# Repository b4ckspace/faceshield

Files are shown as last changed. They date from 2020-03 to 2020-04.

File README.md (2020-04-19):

# Lasercut Face Shield

Due to the Covid-19 outbreak, there is an increased need for face protection for health care professionals and many others. There are multiple projects that are trying to offer makeshift solutions. These are ours.

Our face shields are laser cut which allows producing lots of shields quickly. What makes our v1 and v2 shields different is that we are not cutting the actual shield but use off the shelf A4 or A3 transparency sheets. That way the laser cut pieces can be reused multiple times while only replacing the transparency shield. This is not a new idea but other projects offering this feature are all 3D printed which limits the output.

The sheet is attached with standard pattern holes that can be created with a normal 80mm, Euro pattern hole puncher. Support for 888 patterns or full 4 hole punchers are of benefit.

See our [detailed instructions](hole_patterns.md) on how to create these hole patterns.

## Version 1
Still primitive, uses hollow rivets for construction
Shield Version 1
[Details](v1/)

## Version 2
More sophisticated. Comes with a shield for the fore head. Is more flat at the front. No needs for fasteners.
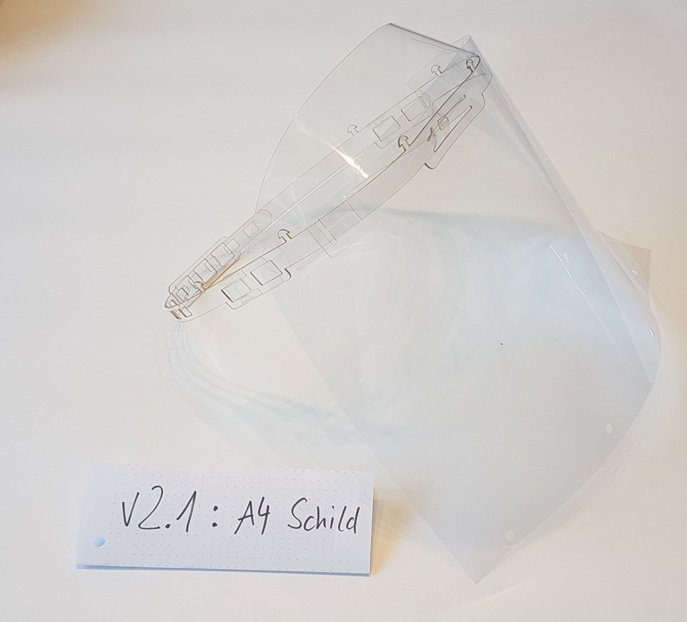
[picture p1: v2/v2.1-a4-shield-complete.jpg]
Shield Version 2.1

[Details](v2/)

## Version 3
A full shield cut from thicker material (0.7mm PET and 0.8mm PP).
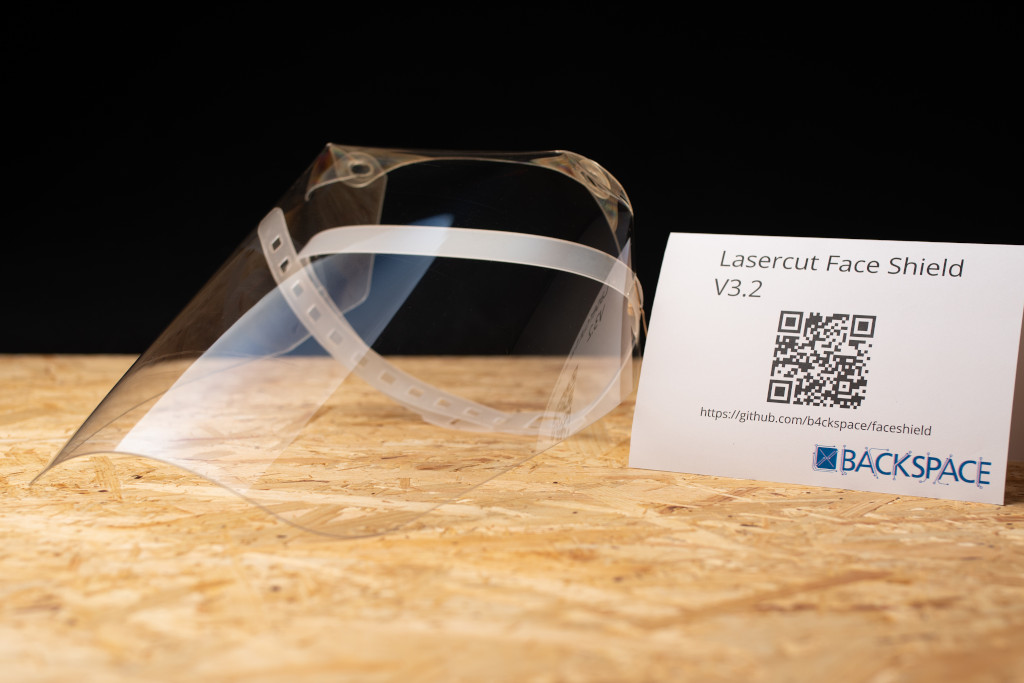
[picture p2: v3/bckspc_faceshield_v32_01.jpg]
Shield V3.2


[Details](v3/)

## Shield from Office Supplies
A shield made only out of an A3 sheets with normal office supplies. No need for a laser cutter or other exotic tools.
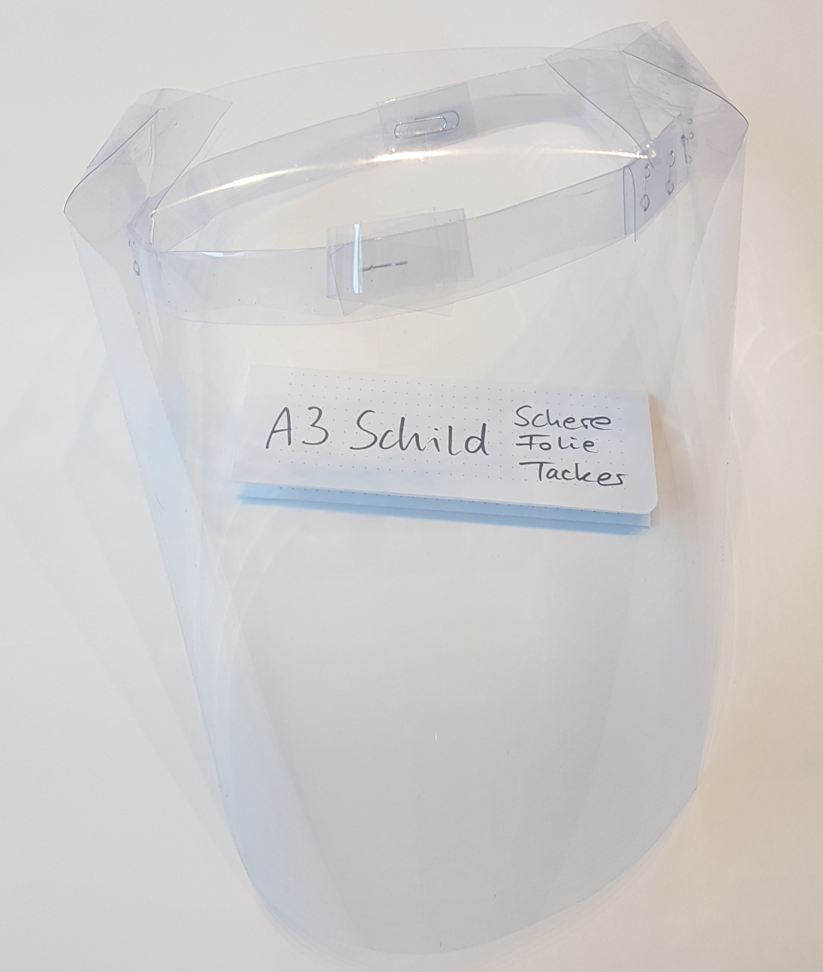
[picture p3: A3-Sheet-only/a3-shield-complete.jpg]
A3 Shield


[Build instructions](A3-Sheet-only/manual.md)

## Status

All variants work quite well, but they depend a lot on the materials used. The different plastics cut and behave quite differently. Polycarbonate ist really tough and cuts well but produces a huge mess and clogs up the filters really fast. The 0.69mm PET has good optical quality but tends to be brittle and a lot of fancy features had to be abandoned for v3 as the material would just break too easily. We are currently using 0.8mm Polypropylene as head straps as it is soft and does not break. This works fine for V3 but might not be stiff enough for an unsupported arc holding an heavy shield in front of the face.

The lesson learned here is that each new material basically requires some new engineering effort.

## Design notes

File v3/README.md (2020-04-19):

# Laser Cut Face Shield V3.2

Shield 3.2

This variant is optimized for the material we had at hand: 0.69mm PET. It is still unclear what is the exact cause but our material tends to break in a brittle way - sometimes. This forces this model to be more primitive and to avoid more clever solutions.

The shield consists of two laser cut parts: The shield itself, made from 0.69mm PET that gets folded inwards at the top and the head strap made from 0.8mm PP which is much softer.

V3.2 cutting pattern

They are connected with two split pin paper fasteners. While they look very unfomfortable they actually barely touch the head of the wearer.

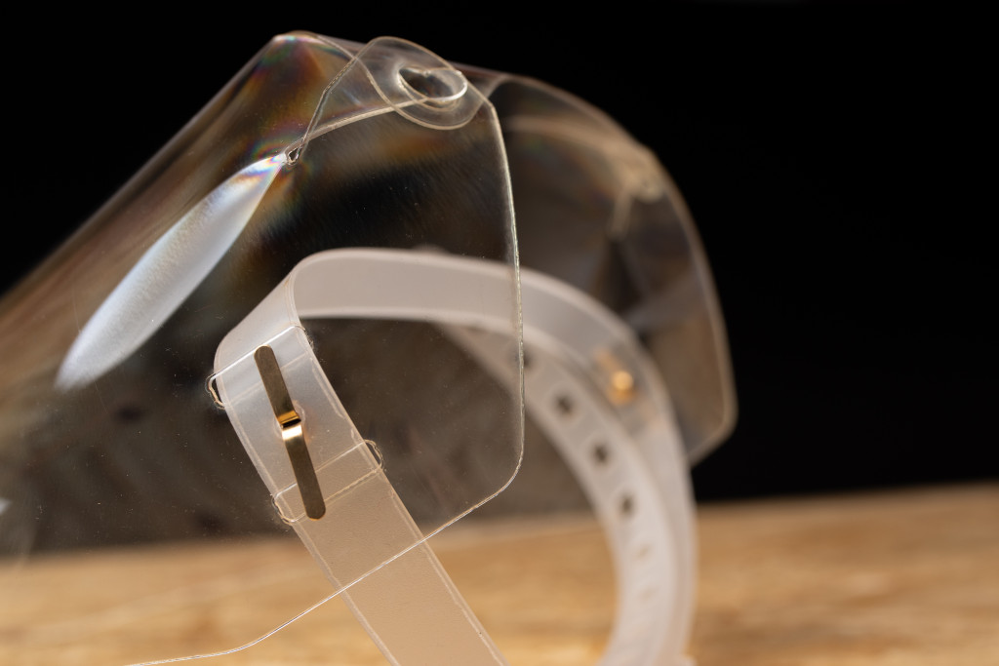
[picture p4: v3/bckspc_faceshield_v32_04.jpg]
Shield details


What sets this shield appart from others:

The shield is bend inwards at the top. This reduces the gap between the shield and the head. It also stiffens the shield and keeps it more flat at the front. This makes it easier to see through and reduces reflections and glares.

No elastic band used. This makes it easier to desinfect. It also allows putting it on with only one hand. So it may be more conviniet in situations where the shield needs to be put on and off very often or very quickly. Size of the head strap can be adjusted easily. The current material we use is on the soft side for this mechanism. It works even better with stiffer materials - either thicker PP or other plastics like PC or PS.

There are multiple intermediate versions that use more clever ways of construction and don't need additional hardware. We will publish them here soon.

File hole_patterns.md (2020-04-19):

# Creating The Right Hole Patterns

Version 1 and 2 are both supporting A4 and A3 sheets. But other sizes can also be used if given the right hole patterns. The basic pattern we use is called 888 or 3x8 and is supported on most Euro hole punchers. This is a pattern of 4 holes with 80mm distance center to center. There are a lot of ways to achive this pattern - depending on the equippement at hand.

## 4 Hole punch

If you need a lot of sheets (e.g. you want to change them often) get a normal 4 hole punch. They are cheap and create the pattern right away.

## Normal 2 Hole Punch With Side Stop

Many hole punchers have an adjustable side stop that does have an 888 or 3x8 setting. You can just use this setting from both sides of the page to get the 4 holes all with the same distance. This **only works** for sheets that are **exaclty A4** in size!

## Measure

You can use a ruler to find the right place to punch the holes. As normal hole punchers typically have a mark for the center of the page you can just mark the spots 80mm left and righ of the page center and align your hole punch there. This has the benefit of also working with sheets that are not 297mm long (A4 landscape)

## Double punch!

If you just have a normal hole punch you can try this:

* Mark the middle of the page
* Punch the center holes
* Use the holes as new centers
* Use the new outer holes as new centers

This gives you a row of holes 40mm apart. Some of them are punched twice. You need to be pretty precise for this to work. Check if the double holes are not missaligned

## A3 Sheets

For the A3 we use the (fictional) 88888 pattern. It is the 888 pattern from above plus two more holes that are also 80mm further out. If you want to use A3 sheets you really should get a 4 hole punch, but you can also use any other methods above - except using a side stop.

The outer holes would be 10mm in from the sides. We moved hooks inward a bit so holes with about 11mm from the sides also work. That way you can just turn you hole punch around and use it from the sides. The hole should be about the same distance from above.

# Other Holders

Note that not everyone is using this pattern. Some 3D printed shields use a 80mm-68.5mm-80mm pattern. It is created by using the A6 side stop settings from both sides on an A4 sheet.

Our design currently does not support this hole pattern. But it can be added easily. Please open a ticket if you are interested.

# Cutting To Shape

All sheets need to be cut into shape to allow head movement. A4 can be used uncut, but is much more comfortable if the lower corners are clipped. A4 sheets offer just enough protection for many use cases.

A3 sheets offer much better protection. But if used in their full size are just too big and don't let enough fresh air in. They need to be cut to size. You want to cut off the bottom corners up to the top edge and probably even shorten it at the bottom. It is difficult to give general advice here as all use cases are different.

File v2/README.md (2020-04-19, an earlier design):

# Face Shield Version 2

Shield V2.1

This also a holder for a transparent sheet. Both A4 and A3 sizes are supported. The two main parts need to be cut from a stiff material. 1 to 1.5mm thickness should work for plastics like Polycarbonate (PC), Polystylol (PS) or PETG. The fore head shield needs to be more elstic. We used .5mm PETG but this can surely be made from even thinner material.

Cuttingpattern

# Assembly

The short strap needs to be put through the inner rectangular holes until the wider part is on the outside. Then turn the strap upright so it cannot get out again. The thinner ends are then put to the next hole to lock the strap in place.

Connect the flaps at the front by twisting them an put the inner ends through the holes at the outside strap.

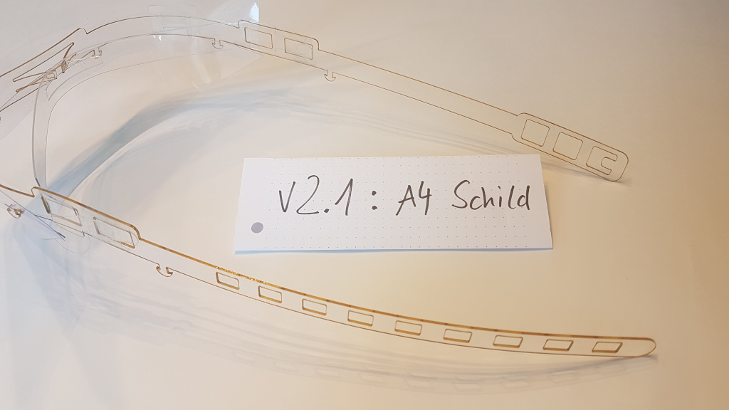
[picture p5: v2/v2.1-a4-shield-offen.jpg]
Details


If you want the front shield to be less round at the bottom you can put two of the small pieces with the mushrooms at the ends into holes on both sides. You need an 888 holes pattern at the bottom of the sheet for this (4 holes each 80mm appart). But we found that to not be necessary.

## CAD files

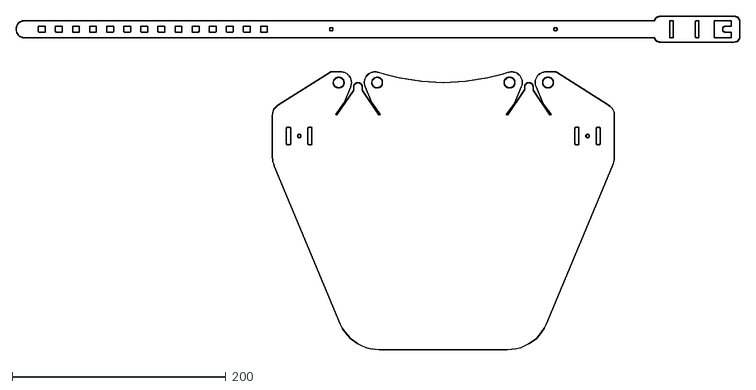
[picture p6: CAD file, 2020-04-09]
v3/faceshield-3.2.dxf
677.6 x 312.0

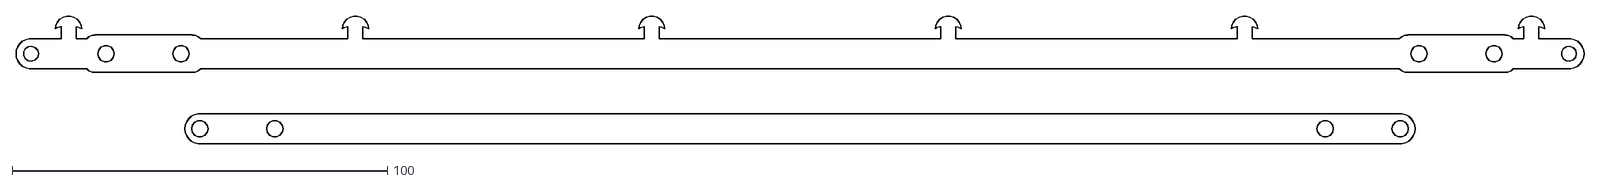
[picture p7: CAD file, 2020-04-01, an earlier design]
v1/faceshield.dxf
418.0 x 34.0

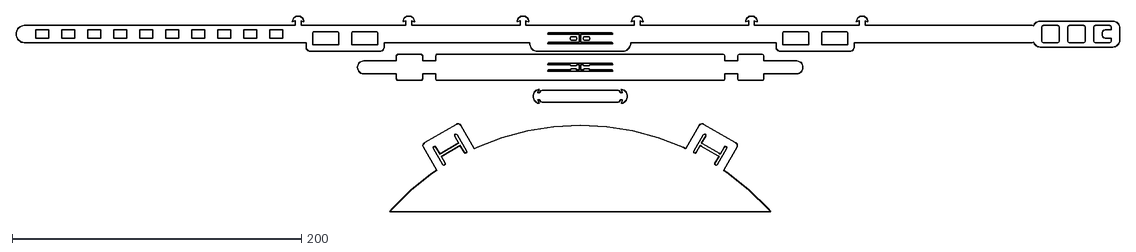
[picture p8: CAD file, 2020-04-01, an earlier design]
v2/faceshield-v2.1.dxf
763.2 x 135.5

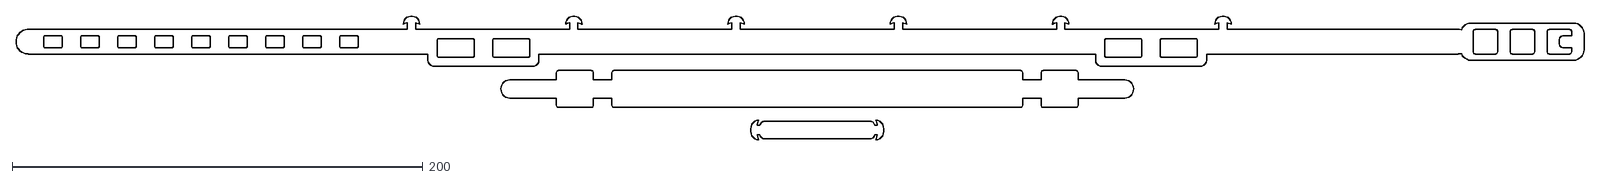
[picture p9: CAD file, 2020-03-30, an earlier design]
v2/faceshield.dxf
763.2 x 60.3

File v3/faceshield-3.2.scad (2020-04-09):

shield_width = 320;
shield_height = 220;

strap_length = 700;
strap_inner = 16;
strap_outer = 24;

$fa = 6;
$fs = .5;

module roundedRectangle(x, y, z, r) {
    difference() {
        cube([x, y, z], center=true);
        for (sx = [-1, 1]) {
           for (sy = [-1, 1]) {
              scale([sx, sy]) {
                translate([x/2, y/2])difference() {
                    cube([2*r, 2*r, 2*z], center=true);
                    translate([-r, -r])cylinder(3*z, r=r, center=true);
                }
              }
            }
        }
    }
}

module clip(wo, wi, f=.2) {
    difference() {
        roundedRectangle(3*wo+(wo-wi), wo, 1, 5);
        //for (x = [-1.5*wo+wi/2:wo/2:1.5*wo-wi/4])translate([x, 0, 0])roundedRectangle(wi/3, wi, 3, 1);
        translate([1*wo, 0, 0])difference() {
            roundedRectangle(wi, wi, 2, 1);
            translate([0.5*wi, 0, 0])roundedRectangle(wi, wi/3, 3, 2);
        }
        roundedRectangle(f*wi, wi, 2, 1);
        translate([-wo, 0, 0])roundedRectangle(f*wi, wi, 2, 1);
    }
}

module strap(lt, l, w, wi) {
    offset = 50;
    union() {
        difference() {
            union(){
                translate([-2*w-offset, 0])roundedRectangle(lt-4*w, wi, 1, wi/2);
                //roundedRectangle(l+40, w, 1, 5); // middle part
                translate([lt/2-2.6*w-offset, 0])clip(w, wi);
                /*
                for (msx = [-1, 1])scale([msx, 1, 1]) {
                    translate([l/2-45, 0, 0])roundedRectangle(20, wi+8, 1, 1);
                }*/
            }
            /*
            for (i = [-1, 1])for (j = [-1, 1])scale([i, j, 1]) {
                translate([l/2-15, wi/2+1])roundedRectangle(30, 2, 2, 1);
                translate([l/2-15, -(wi/2+1)])roundedRectangle(30, 2, 2, 1);
                difference() {
                    translate([l/2-15, wi/2+(w-wi)/4+1])cube([10, (w-wi)/2-2, 2], true);
                    translate([l/2-10, wi/2+(w-wi)/4+1])cylinder(5, d=(w-wi)/2-2, true);
                    translate([l/2-20, wi/2+(w-wi)/4+1])cylinder(5, d=(w-wi)/2-2, true);
                }

            }
            */
            for (x = [-lt/2-offset+w:wi:-l/2-25]) translate([x, 0])roundedRectangle(0.4*wi, wi/3, 2, 0.5);
            for (i = [-1, 1])scale([i, 1, 1]) {
                translate([l/2-25, 0])cylinder(3, d=3.1, center=true);
                /*
                translate([l/2-15, 0])roundedRectangle(1, wi/3+2, 2, 0.5);
                for (j = [-1, 1])scale([1, j, 1]) {
                    translate([l/2-5-4.5, wi/6+0.5])roundedRectangle(12, 1, 2, 0.5);
                }
                
                translate([l/2-25, 0])roundedRectangle(1, wi/3+2, 2, 0.5);
                for (j = [-1, 1])scale([1, j, 1]) {
                    translate([l/2-35+4.5, wi/6+0.5])roundedRectangle(12, 1, 2, 0.5);
                }
                */              
            }
        }
        difference() {
            for (i = [-1, 1])scale([i, 1, 1]) {
                translate([20, 0, 0])roundedRectangle(30, w/2, 1, 2);
                translate([5, 0, 0])roundedRectangle(9, 10, 1, 1);
            }
            for (i = [-1, 1])scale([i, 1, 1]) {
                // inner connection
                translate([3, 0, 0])roundedRectangle(0.6, w/8, 2, 0.05);
            }
        }
    }
}

module strap2(lt, l, w) {
    difference() {
        roundedRectangle(lt, w, 1, w/2);
        translate([-lt/2+120+25, 0, 0])cylinder(2, d=5.5, center=true);
        translate([-lt/2+120+l-25, 0, 0])cylinder(2, d=5.5, center=true);
    }
}

module shield(w, h, s=20) {
    union(){
        difference() {
            hull() {
                for (sx = [-1, 1])scale([sx, 1, 1]) {
                    translate([60, 40,])cylinder(1, r=40);
                    translate([w/2-20, h-40, 0])cylinder(1, r=20);
                    translate([w/2-10, h,])cylinder(1, r=10);
                    translate([105, h+40-2,])cylinder(1, r=2);
                    
                }
                
            }
            for (sx = [-1, 1])scale([sx, 1, 1]) {
                // Strap
                //translate([w/2, h-20])roundedRectangle(10, si, 2, 0.5);
                translate([w/2-35, h-20])
                    roundedRectangle(4, s, 2, 1);
                translate([w/2-15, h-20])
                    roundedRectangle(4, s, 2, 1);
                translate([w/2-25, h-20])
                    cylinder(2, d=3.1, true);
                /*
                translate([w/2-35, h-20+(so/2-(so-si)/4+1)])
                    roundedRectangle(4, (so-si)/2, 2, 1);
                translate([w/2-35, h-20-(so/2-(so-si)/4+1)])
                    roundedRectangle(4, (so-si)/2, 2, 1);
                */
                /*
                translate([w/2-35, h-20-si/4, 0])roundedRectangle(30, 3, 2, 1);
                translate([w/2-20, h-20, 0])roundedRectangle(2, si+1, 2, 1);
                translate([w/2-50, h-20, 0])roundedRectangle(2, si+1, 2, 1);

                translate([w/2-35, h-20-si, 0])roundedRectangle(51, 1, 2, .5);
                translate([w/2-10, h-19-si*3/4, 0])roundedRectangle(1, si/2+2, 2, .5);
                translate([w/2-60, h-19-si*3/4, 0])roundedRectangle(1, si/2+2, 2, .5);
                */
                // top fold
                translate([80, h+20, 0])cube([50, 40, 2], true);
            }
            translate([0, h+230])cylinder(3,d=400, true);
        }
        // top fold
        for (sx = [-1, 1])scale([sx, 1, 1]) {
            translate([80, h+10, 0])roundedRectangle(8, 40, 1, 4);
            hull() {
                translate([80, h+20, 0])cylinder(1, d=10);
                translate([80, h-1, 0])cube([40, 1, 1], true);
            }
            difference() {
                hull() {
                    translate([105, h+39, 0])cylinder(1, d=2);
                    translate([95, h+12, 0])cylinder(1, d=4.5);
                    translate([104, h, 0])cylinder(1, d=5);
                    translate([96, h+30, 0])cylinder(1, d=20);
                    
                }
                translate([98, h+30, 0])cylinder(1, d=10);
            }
            difference() {
                hull() {
                    translate([55, h+36.7, 0])cylinder(1, d=2.3);
                    translate([65, h+12, 0])cylinder(1, d=4.5);
                    translate([56, h, 0])cylinder(1, d=5);
                    translate([64, h+30, 0])cylinder(1, d=20);
                    
                }
                translate([62, h+30, 0])cylinder(1, d=10);
            }
        }
    }
}

projection()strap(strap_length, shield_width-60, strap_outer, strap_inner);
projection()translate([0, -300, 0])shield(shield_width, shield_height, strap_inner);

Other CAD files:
v1/faceshield.scad
v2/faceshield.scad

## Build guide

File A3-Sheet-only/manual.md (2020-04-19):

# Face shield from one single A3 sheet

With the COVID-19 outbreak, there are multiple projects that provide a face shield. But they often rely on 3D printed or laser cut parts that are not available to everyone. These instructions allow building a decent face shield from just office supplies. While maybe not as fancy it still provides good protection, is stable enough and provides good comfort. It is also probably one of the lightest face shields available.

A3 Shield

You need:

* Transparent A3 sheet about 0.2mm thick
* Ruler
* Scissors
* Knife
* Stapler
* Tape

Instructions:

* Cut sheet as shown in the SVG
 * There are two variants: [One with hints for assembly](A3-cutting-pattern.svg) and [one with only the cutting lines](A3-cutting-pattern-print.svg)
* Fold both 4cm stripes along their length
* Then overlap them for a few centimeters and join them with two staples
* Put the thin 2cm stripe through the 2cm slits in the middle.
  * Secure with a bit of tape as shown
  * The side with the tape is now the outside
* Staple the strip inside to the left where shown with two or three 
  * Have the staples joining the stripes right inside of the staple area
  * Make sure the strip is parallel to the top and bottom edge
* Staple the strip to the right side but make the strip 8 cm shorter than the shield
  * The sides of the shield should bend backward
* Bend the top of the sheet at the 4cm cuts so the sides and the top bend inwards
  * Make sure the 4x4cm tab is on the inside
  * Let the corners of the outside parts touch
  * Then secure with a piece of tape
  * Do the same for the other side
* Bend the 2cm strip into a loop that keeps the shield about 2cm from the strap
  * Staple the loop to the strap

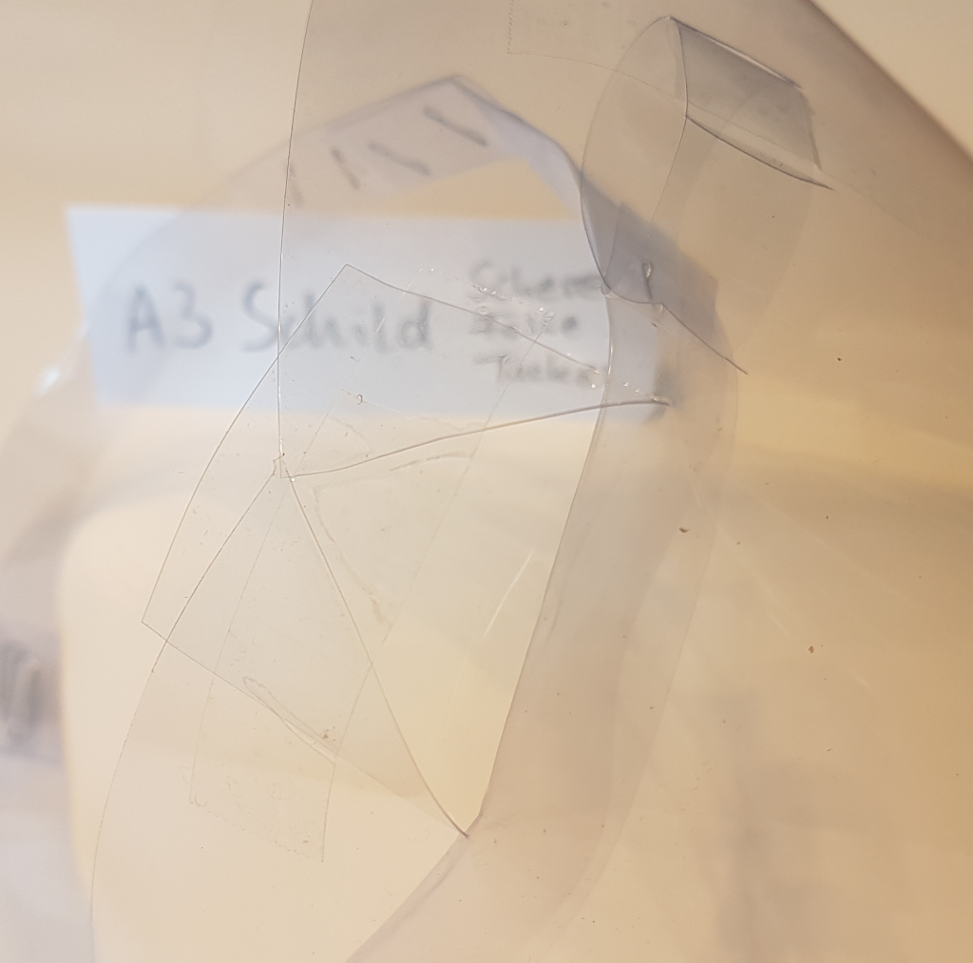
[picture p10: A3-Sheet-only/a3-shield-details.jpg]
Details


* Put on the mask and adjust the length of the strap
* You can now either:
  * Secure it with one staple
* or
  * Make 5mm shorter
  * Punch a hole through both straps
  * Secure with a paper clip 

You are done! Stay healthy!

cutting schematic

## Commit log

2020-03-26 Version 1
    [faceshield.scad]
2020-03-29 Add reinforment patch and make length dependent on holes
    [faceshield.scad]
2020-03-29 Try to narrow down to allow thicker material to be used.
    [faceshield.scad]
2020-03-30 Fix typo
    [faceshield.scad]
2020-03-30 v2 initial commit
    [faceshield.dxf, faceshield.scad]
2020-03-31 Connect inner and outer strap to make shield more straight at the front
    Add a forehead shield
    [faceshield.scad]
2020-03-31 Rendered version 2.1
    [faceshield-v2.1.dxf]
2020-04-01 Move A3 mushrooms further in
    to allow punching the holes from the sides
    [faceshield-v2.1.dxf, faceshield.scad]
2020-04-01 Fix wrongly fixed typo
    [faceshield.scad]
2020-04-09 v3.2 Full shield with laser cut strap
    Made for 0.7mm PET shield and 0.8mm PP strap
    [faceshield-3.2.dxf, faceshield-3.2.scad]
2020-04-19 Instructions for hole patterns
